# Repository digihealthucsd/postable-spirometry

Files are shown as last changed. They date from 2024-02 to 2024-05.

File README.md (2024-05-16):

# postable-spirometry: User-Assembled Vortex Whistle Spirometer

## About Project:
3D printed vortex whistles have been shown to be an accessible alternative to clinical spirometers, the most common pulmonary function test to assess lung health. While more accessible than the current standard, the question remains of how to get the whistles to users for their own personal use. The novelty of this project is the proposal and demonstration of our idea of making the vortex whistle out of a postcard so it can be simply mailed to users. This work demonstrates the potential for a spirometer system to be mass-deployed in the form of a postcard. The results demonstrate that the use of oilboard does not compromise the performance of the device, and can thus serve as a mass-screening tool. As such, Postable Spirometry can serve as a truly ubiquitous pulmonary function testing solution. This work inspires the larger vision that other smartphone accessories or attachments can also be constructed out of paper, creating a fleet of Postables. Postables will enable the wide scale deployment of ubiquitous smartphone accessories.

## About this repo:
In an effort to open source our work to share our progress with others, this repo contains software [coming soon!] used for analysis (frequency to flow velocity pipeline) as well as the hardware designs. The laser cut designs, and settings to print with, can be viewed and accessed by users. Feel free to print these designs on your own machines and try it out!

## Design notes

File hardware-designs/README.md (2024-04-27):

# FILES

The "hardware-designs" folder contains the following folders and contents:

* .../3d-print: Solidworks and STL files for 3D printed version of the vortex whistle
* .../dxf: Drawing files which can be used for laser cutting of the Oilboard and Sticker Paper parts
* .../postcard: Single SVG file with the main oilboard components and QR code for the postcard
* .../solidworks: Solidworks part and drawing files of the whistle components
* .../assembly-guide: Example assembly guide for the postcard design

# DESIGN

## Main Design

The Oilboard Core and Sticker Paper Outlet Skin files comprise the drawings needed for the laser cut components of the low cost vortex whistle. All dimensions were initially based upon the spirocall paper (https://dl.acm.org/doi/10.1145/2858036.2858401), but has been slightly modified through iterations of the project. They generally remain similar to their original dimensions in the Spirocall paper. Additionally, a funnel component exists to adapt the whistle inlet to a conventional spirometer inlet/ mouthpiece size.
\
\
In order to created a more streamlined process for users, the postcard design contains all needed pieces in a single image file. An example can be found [here](postcard) (at ".../postcard/postableSpirometry.svg"). Additionally, this postcard design could include a QR code which links to an assembly guide to aid users in assembly of the whistle.
\
\
The process of assembly consists of taking the oilboard core pieces and putting them together in the same shape as a 3D printed vortex whistle model. To tape pieces together and seal connections to be airtight, use waterproof medical adhesive tape (very thin, flexible, amazon link below for reference). The sticker paper is used to seal the outlet of the whistle and join it to the top face of the whistle (labeled base 3). An example assembly guide can be found [here](assembly-guide) (at ".../assembly-guide")

## Components

The oilboard core is the primary structure for the whistle. It consists of the following parts:

* Base 1: Main section/body of the whistle which is folded into a cylidrical shape, joining the 35mm sides.
* Base 2: Lower face of the whistle which joins to base 1. No internal circle.
* Base 3: Upper face of the whistle which join to base 1 and the outlet. Has internal circle for outlet.
* Outlet: Outlet nozzle which sits on top of base 3. Fold to join the 27mm sides
* Inlet: Inlet nozzle with tabs to fold outward to seat better in the main whistle body, and also create the needed angle for the entering air. The two thinner tabs are to be joined together when folding the inlet and face the top of the whistle when the inlet is seated in base 1 (through the small hole cutout).
* Funnel: Funnel component to slot over the whistle inlet and adapt it to a larger spirometer mouthpiece size

The sticker paper skin for the outlet replaces a thin tape seal on the outlet, and also has tabs which are folded back during construction. When joining base 3 and the outlet, these sticker paper tabs hold both pieces together, before the thin tape is added on top for a better air seal. 

## Materials

The following information is additional information in regards to the material and laser cut settings used in the project:

* Oilboard: N/A
* Sticker paper: PPD-36
* Laser Cutter: Epilog Laser Cutter

### Epilog Laser Cutter Software Material Configurations:

Oilboard Settings: Oilboard vector preset: 
* Power: 50
* Speed: 45  
* Frequency: 5

Sticker Paper Settings: 
* -Power: 100
* -Speed: 65  
* -Frequency: 5

### Other Materials Notes

Ensure that the glossy side is facing down on the laser cutter (the paper side should face the laser beam). This helps to ensure the cut goes through properly.

Amazon Link to waterproof medical adhesive tape: https://www.amazon.com/Transparent-Adhesive-Waterproof-Bandages-Dressing/dp/B08CXMCPG7/ref=sr_1_15?keywords=medical+tape+waterproof&qid=1692652463&sr=8-15

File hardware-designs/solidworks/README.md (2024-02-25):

The "Solidworks" folder contains the following types of files:

* .SLDDRW: Main drawing files which can be used to create the laser cutter drawings of the whistle components
* .SLDPRT: Dependency files referenced in the .SLDDRW files for the drawings of Oilboard core components

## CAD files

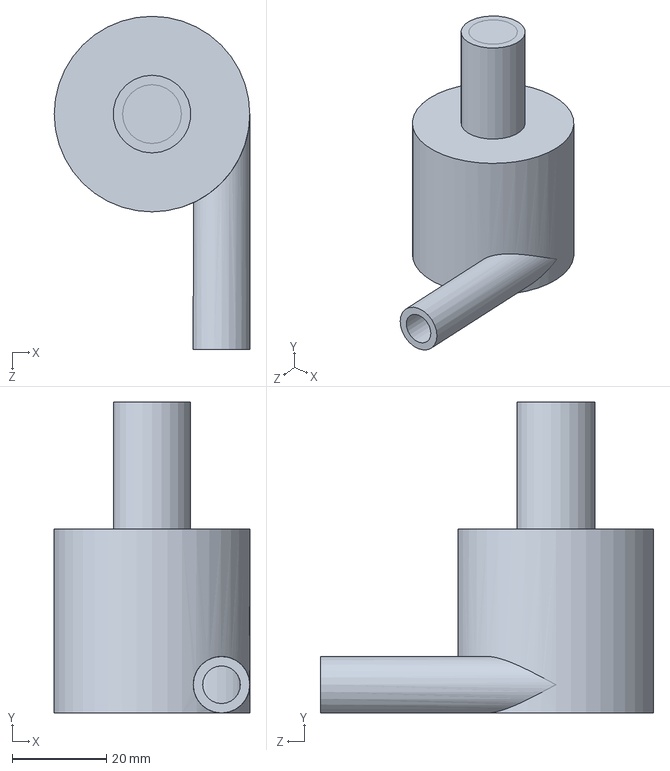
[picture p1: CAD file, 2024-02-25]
hardware-designs/3d-print/3D Print Vortex Whistle.SLDPRT
41.5 x 66.0 x 70.8 mm

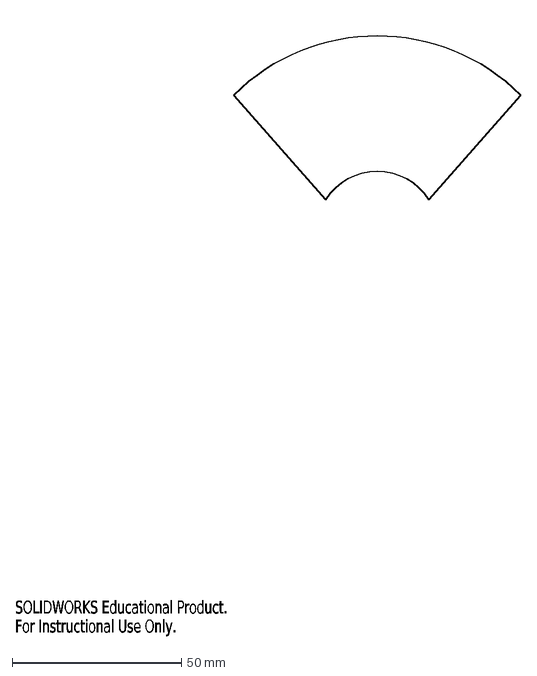
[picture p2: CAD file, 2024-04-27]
hardware-designs/dxf/Funnel.DXF
SOLIDWORKS Educational Product.
For Instructional Use Only.

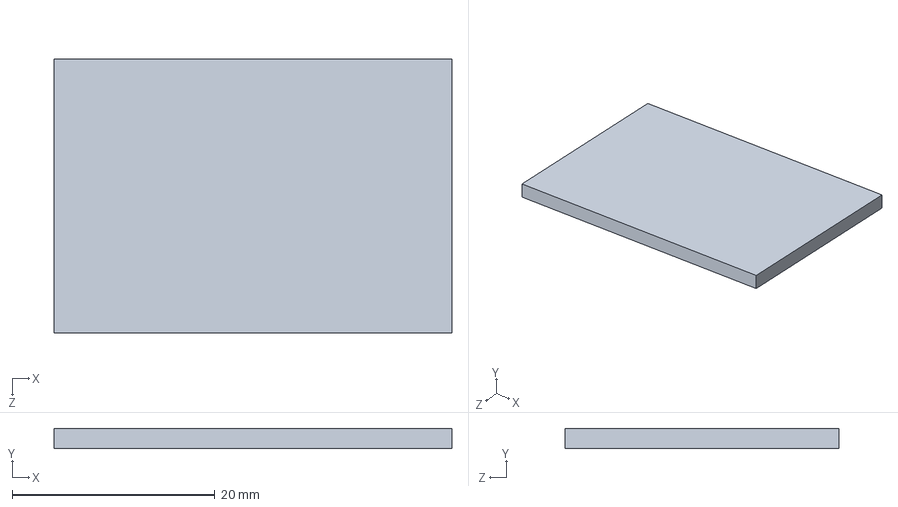
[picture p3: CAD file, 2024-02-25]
hardware-designs/solidworks/Core Outlet.SLDPRT
39.3 x 2.00 x 27.0 mm

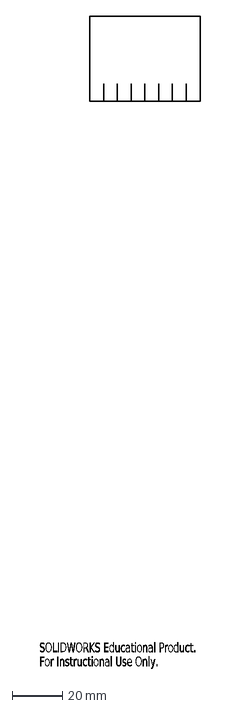
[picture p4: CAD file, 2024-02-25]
hardware-designs/dxf/Sticker Paper Outlet Skin Laser Cut Template.DXF
SOLIDWORKS Educational Product.
For Instructional Use Only.

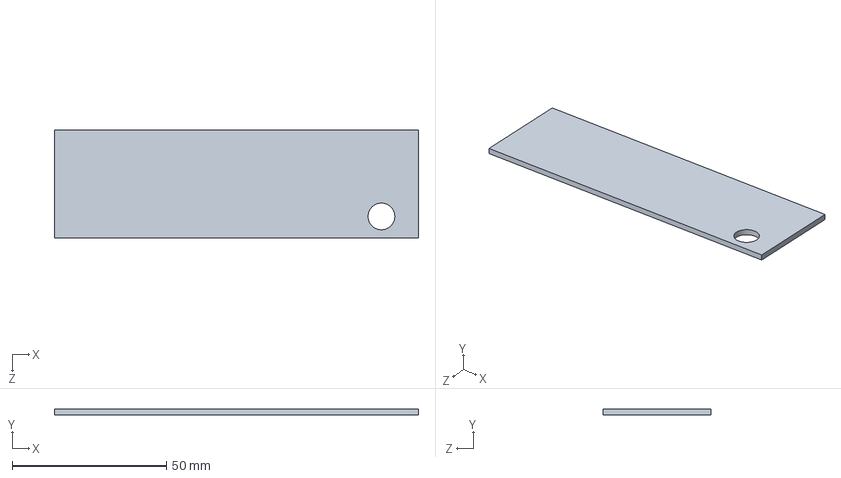
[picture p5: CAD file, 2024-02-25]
hardware-designs/solidworks/Core Base 1.SLDPRT
117.8 x 2.00 x 35.0 mm

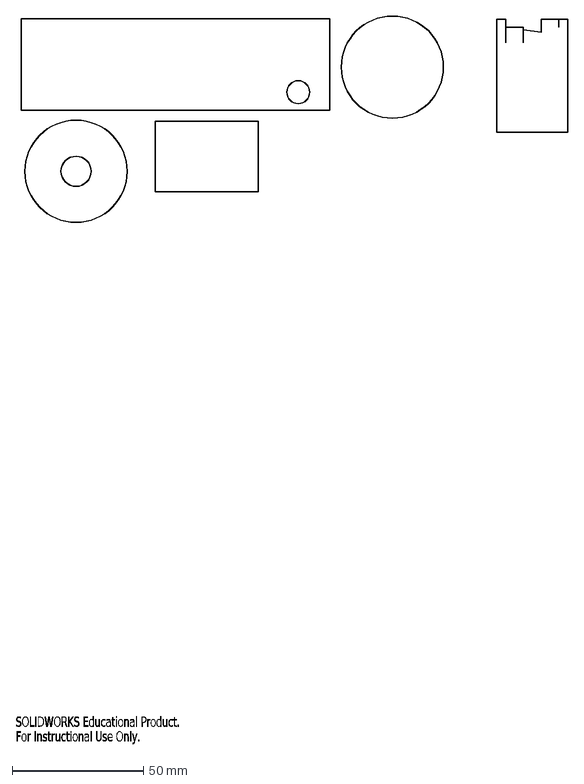
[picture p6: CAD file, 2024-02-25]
hardware-designs/dxf/Oilboard Core Laser Cut Template .DXF
SOLIDWORKS Educational Product.
For Instructional Use Only.

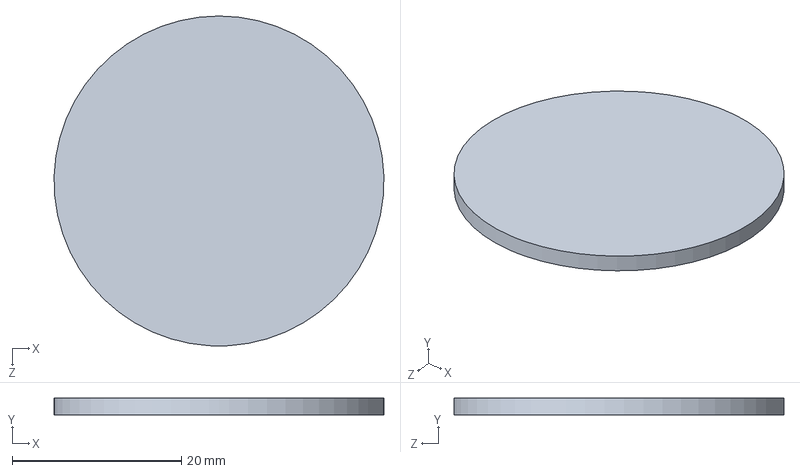
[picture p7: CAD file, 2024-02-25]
hardware-designs/solidworks/Core Base 2.SLDPRT
39.0 x 2.00 x 39.0 mm

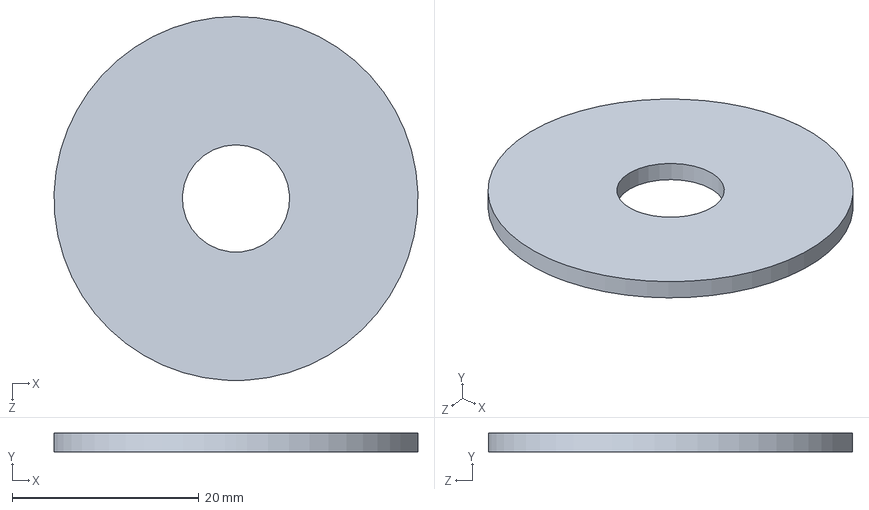
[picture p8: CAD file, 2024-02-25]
hardware-designs/solidworks/Core Base 3.SLDPRT
39.0 x 2.00 x 39.0 mm

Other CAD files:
hardware-designs/3d-print/3D Print Vortex Whistle.STL
hardware-designs/solidworks/Funnel.SLDDRW
hardware-designs/solidworks/Oilboard Core Laser Cut Template .SLDDRW
hardware-designs/solidworks/Sticker Paper Outlet Skin Laser Cut Template.SLDDRW

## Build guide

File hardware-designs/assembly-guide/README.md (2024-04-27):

# Introduction

This assembly guide contains a potential assembly process for creating a postable vortex whistle. This guide contains the steps needed to create a model using only waterproof tape, and an alternative step if the sticker paper cover for the outlet is instead used.

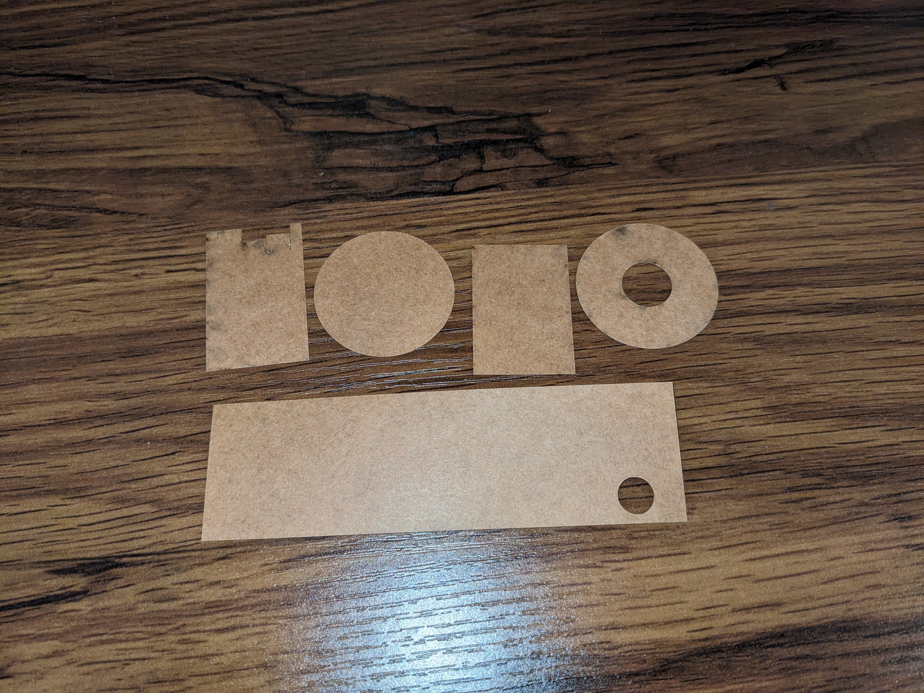
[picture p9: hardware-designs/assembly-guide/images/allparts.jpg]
all_parts


* Starting layout of all oilboard core components

# Assembly Guide

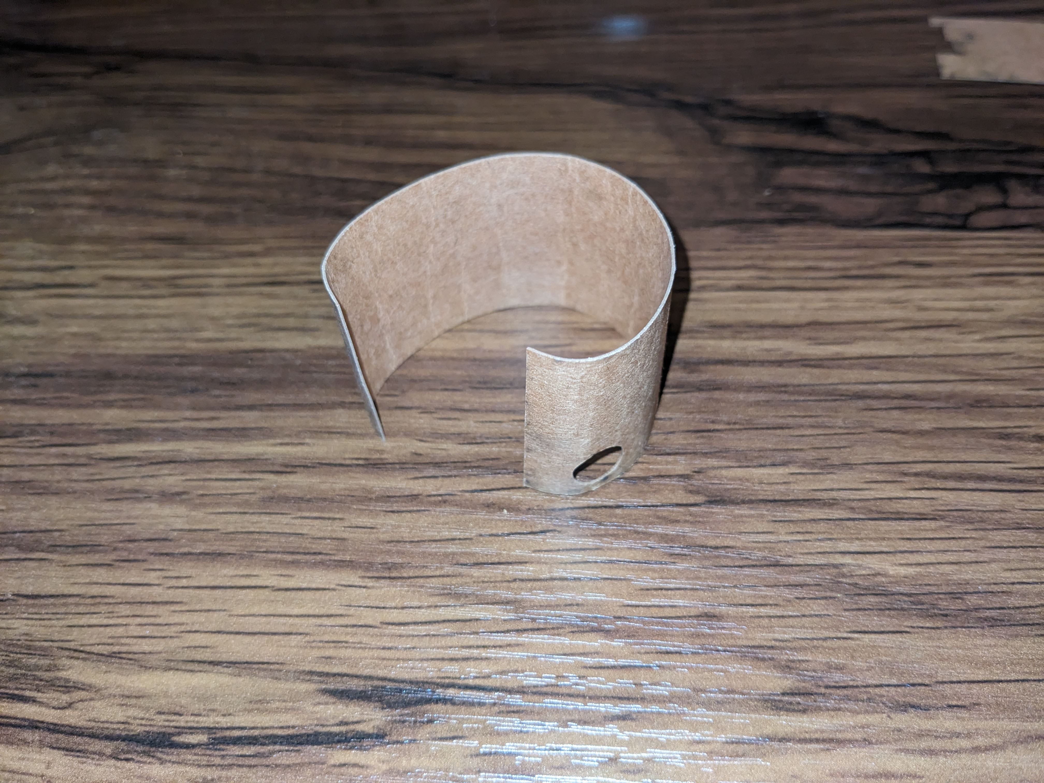
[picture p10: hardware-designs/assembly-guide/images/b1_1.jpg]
fold_body_1

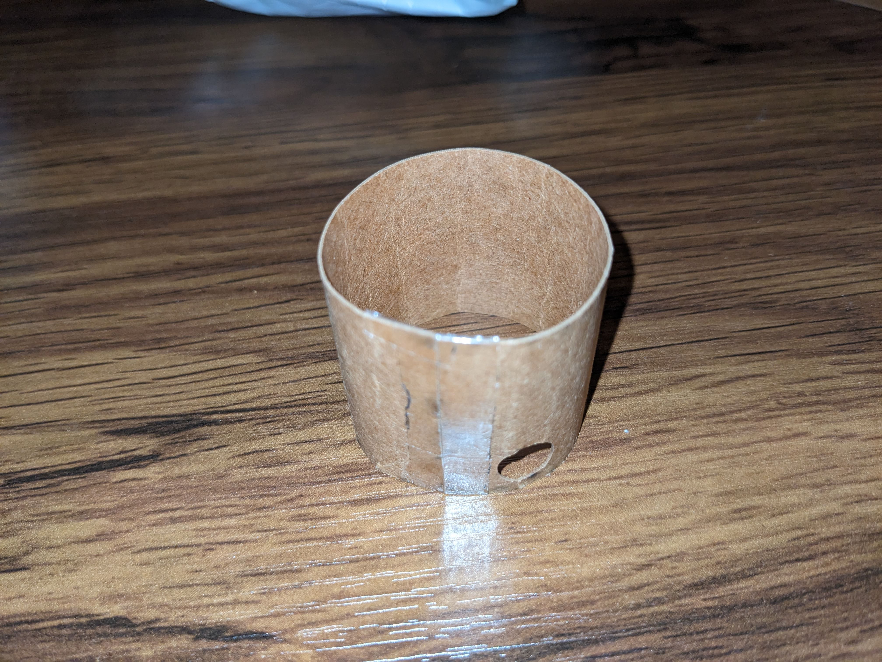
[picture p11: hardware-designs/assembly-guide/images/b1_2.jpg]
tape_body_1


1. Start by folding the main whistle body (body-1 component) piece, then tape the gap to form a cylinder

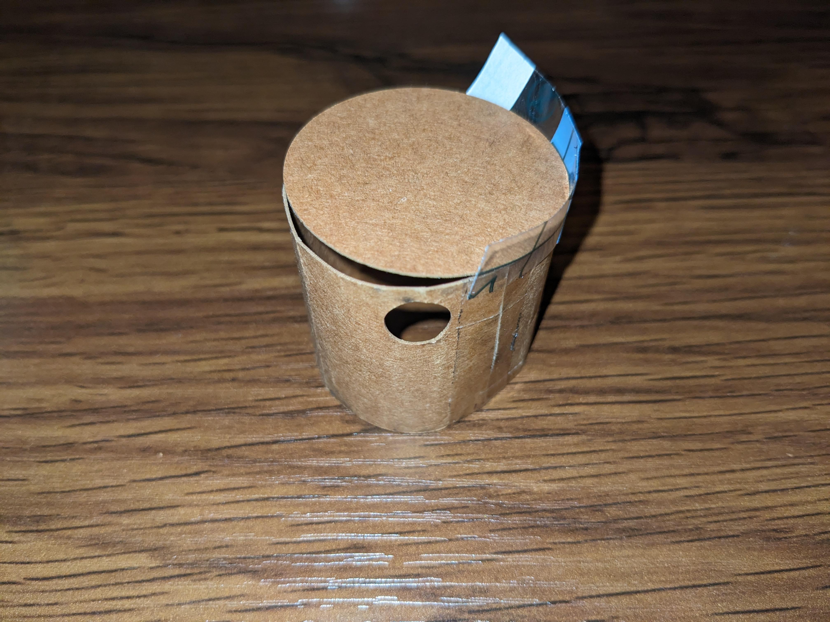
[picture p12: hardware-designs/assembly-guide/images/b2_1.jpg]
tape_body_2

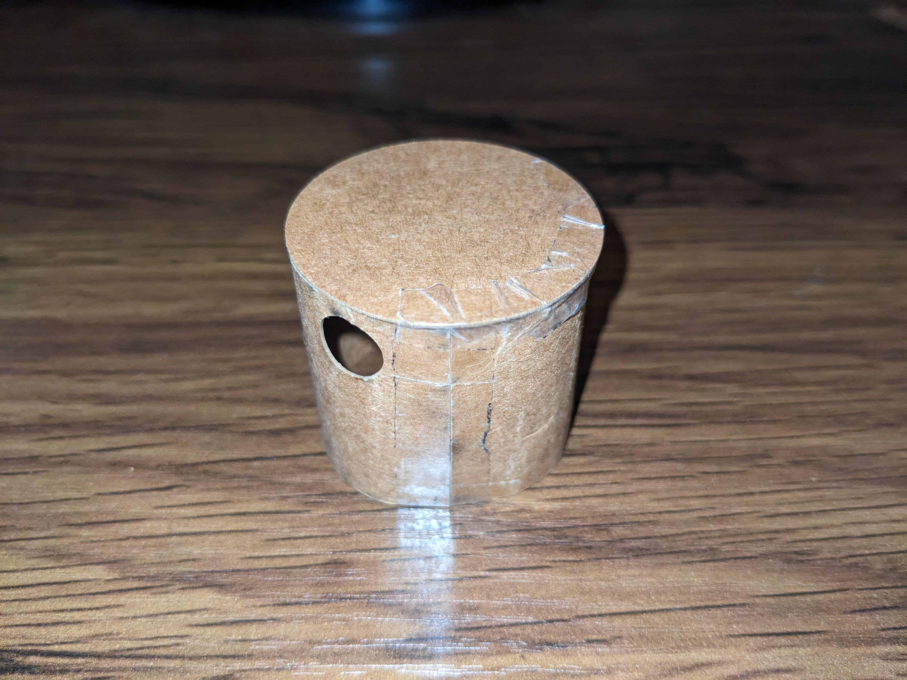
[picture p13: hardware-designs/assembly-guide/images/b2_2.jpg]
seal_body_2


2. Place the lower base (body-2 component) piece on the whistle main body and add tape. Fully seal the seam/gap between the pieces

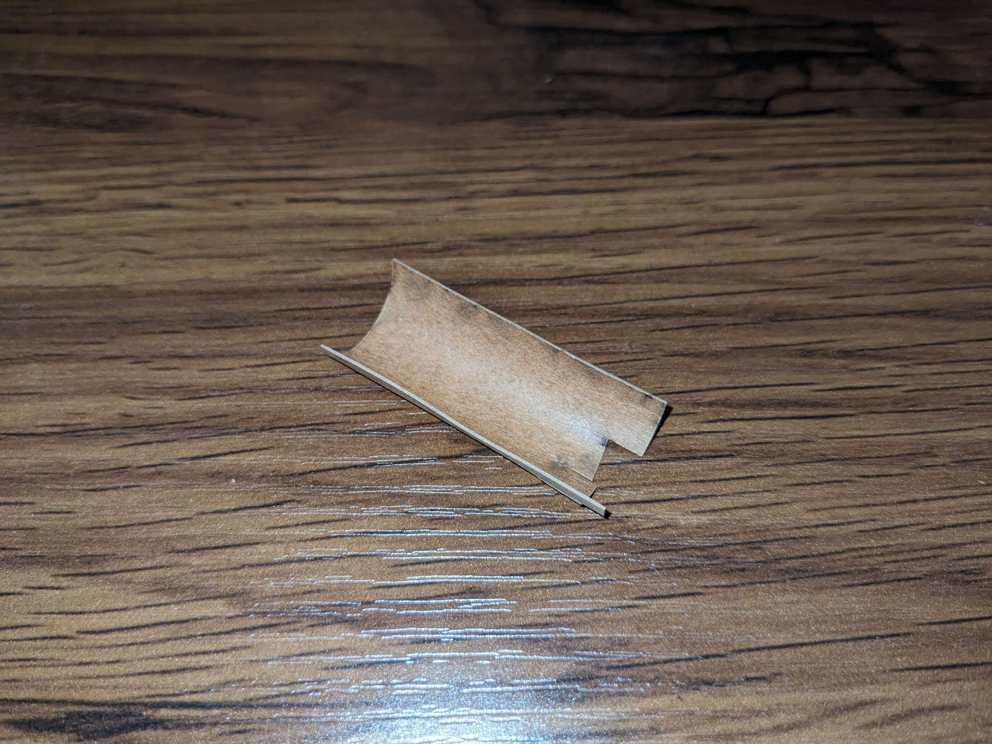
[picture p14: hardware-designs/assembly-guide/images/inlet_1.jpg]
fold_inlet

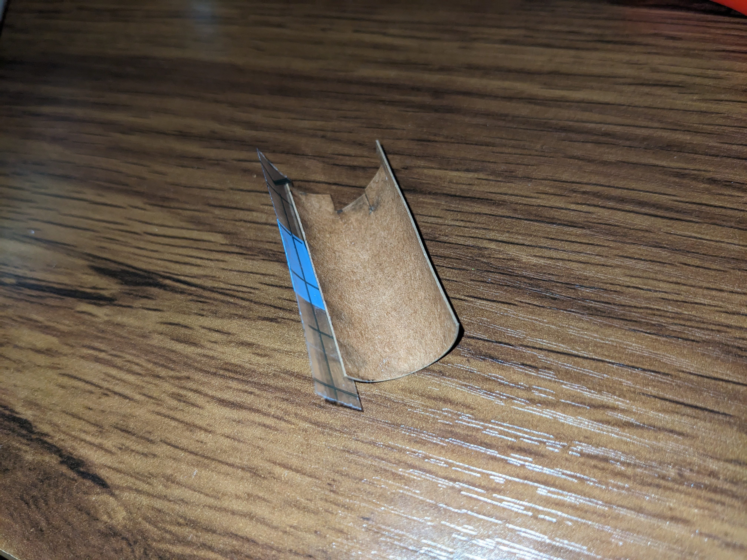
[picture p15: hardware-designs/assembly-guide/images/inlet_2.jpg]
seal_inlet

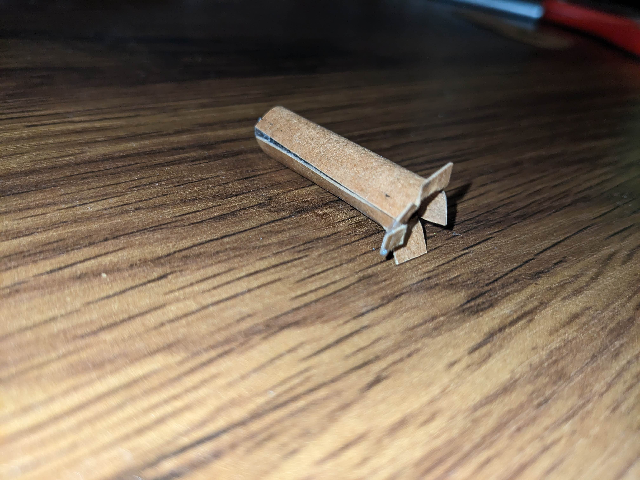
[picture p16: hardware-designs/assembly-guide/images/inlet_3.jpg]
bend_inlet_tabs


3. Fold the inlet piece, seal the main seam to form the cylinder shape of the inlet and then bend the tabs back slightly (this will help with seating the inlet later on).

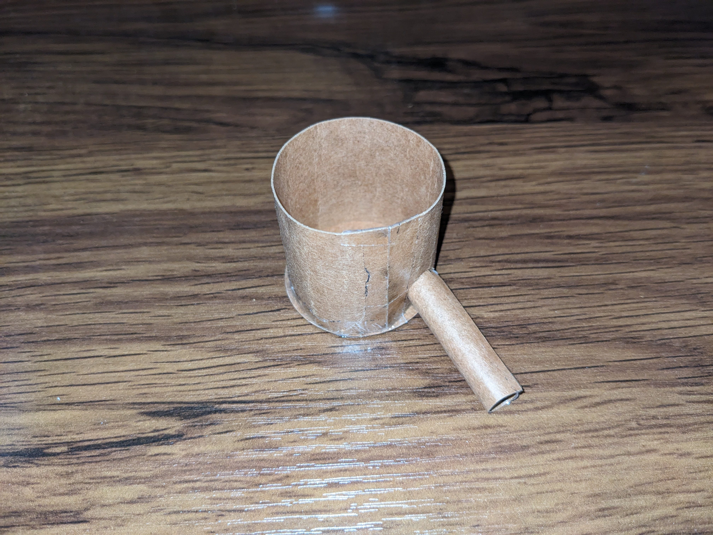
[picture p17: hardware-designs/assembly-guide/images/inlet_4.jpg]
insert_inlet


4. Insert the inlet into the main body piece through the small hold in the main body, being careful not to damage the seal between the main body and lower base. This may require bending the tabs of the inlet slightly to have the inlet fit through the hole.

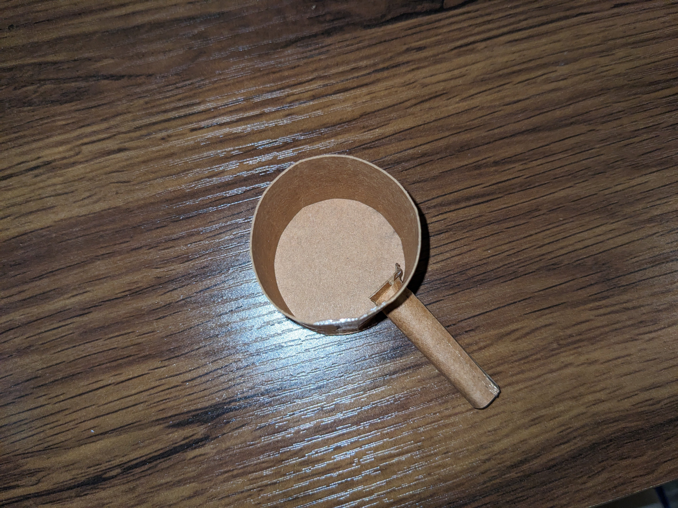
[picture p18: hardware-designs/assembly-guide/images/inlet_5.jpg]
bend_inlet_tabs_back


5. Once the inlet is passed through the hold in the body, press the tabs back outward, and make them flush with the inner wall of the main body.

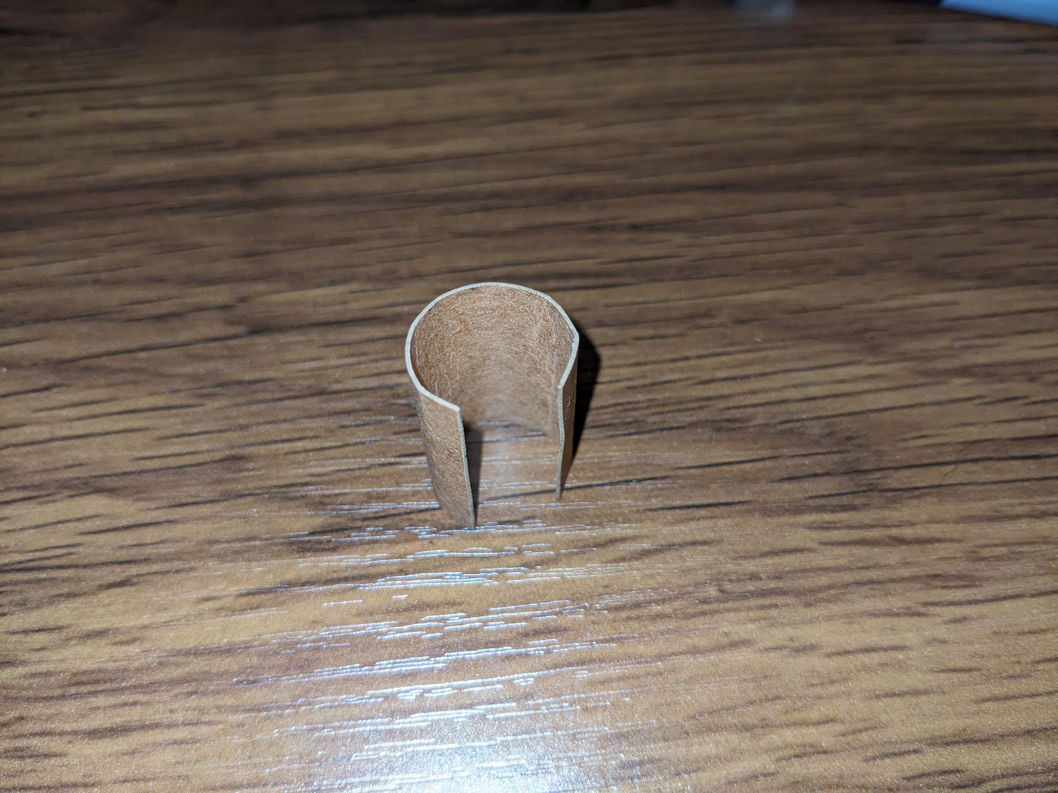
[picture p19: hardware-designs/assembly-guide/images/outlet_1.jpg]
fold_outlet

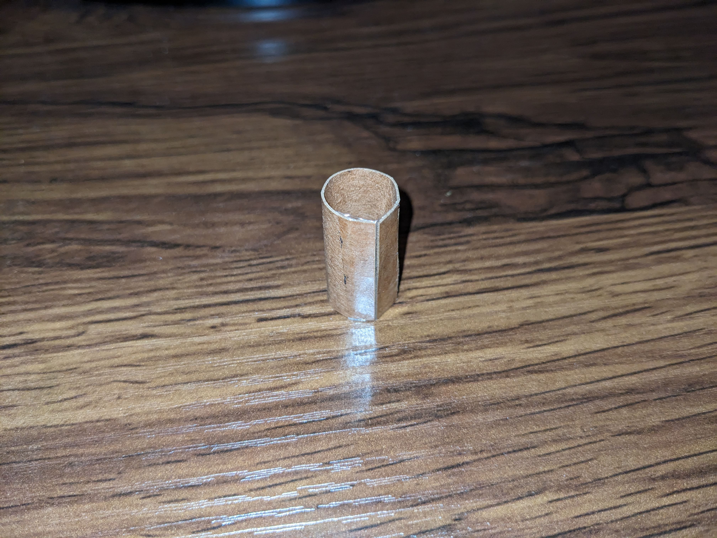
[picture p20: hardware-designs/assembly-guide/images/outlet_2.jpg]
seal_outlet


6. Fold the outlet and seal the seam to form a cylinder.

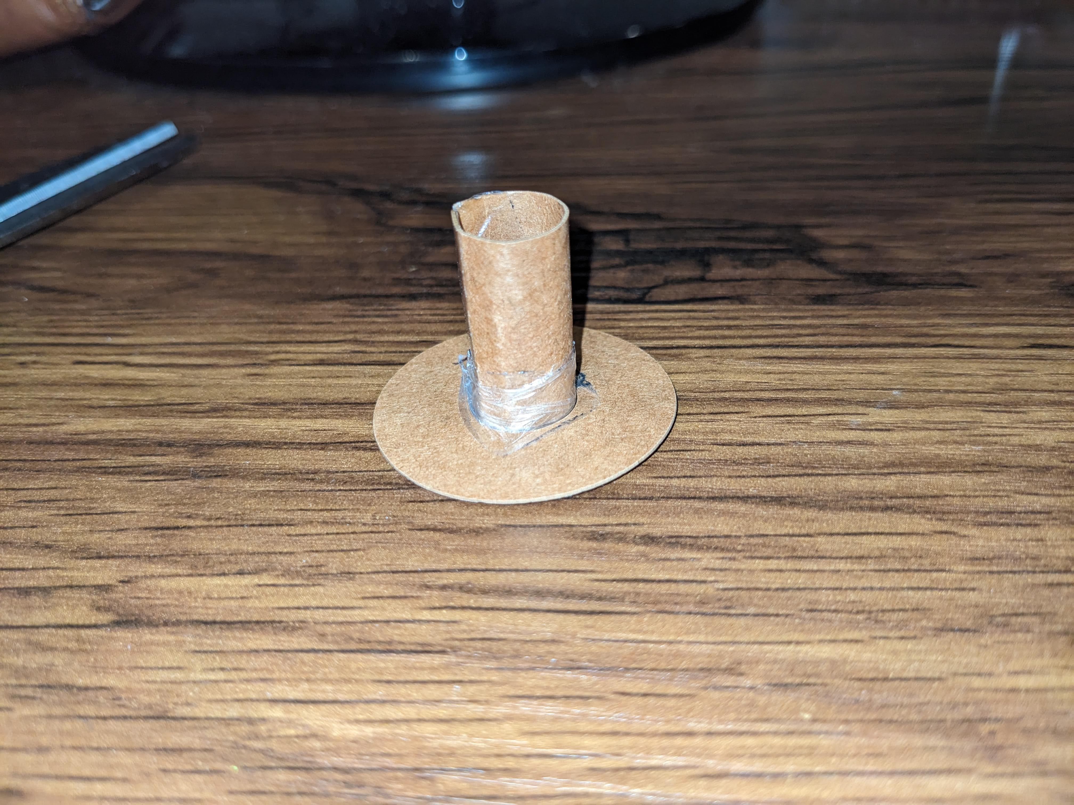
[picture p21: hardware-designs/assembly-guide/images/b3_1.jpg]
join_outlet_body3


7. Tape the outlet to fit over the inner hole of the upper base (body-3 component) of the whistle.
   * (Optional) If desired for use, the sticker paper skin can be instead applied around the outlet, with the tabbed pieces folded back. When joining these pieces, the tabs will be flush with and stick to the surface of the upper base. Tape can then be applied over the same seam of the components to ensure a proper seal between the upper base and outlet.

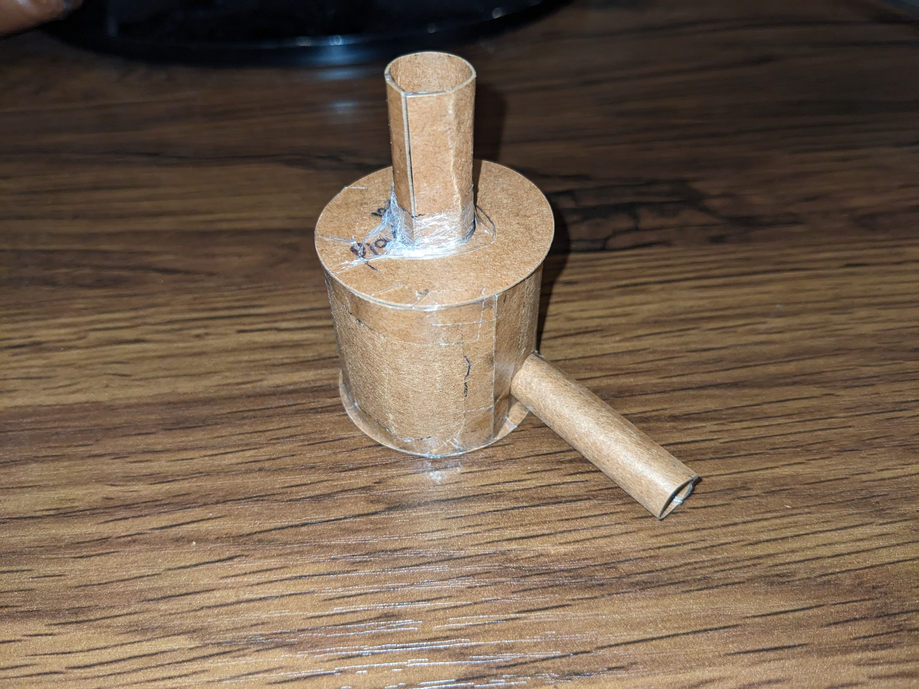
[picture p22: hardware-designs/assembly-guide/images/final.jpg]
finish_whistle
  

8.  In a similar process to the lower base (body-2) component, tape the upper base piece to the top of the main body, ensuring no gaps.
   * To increase air tightness of the device, tape can be added around the gap between the inlet and the main body if desired.

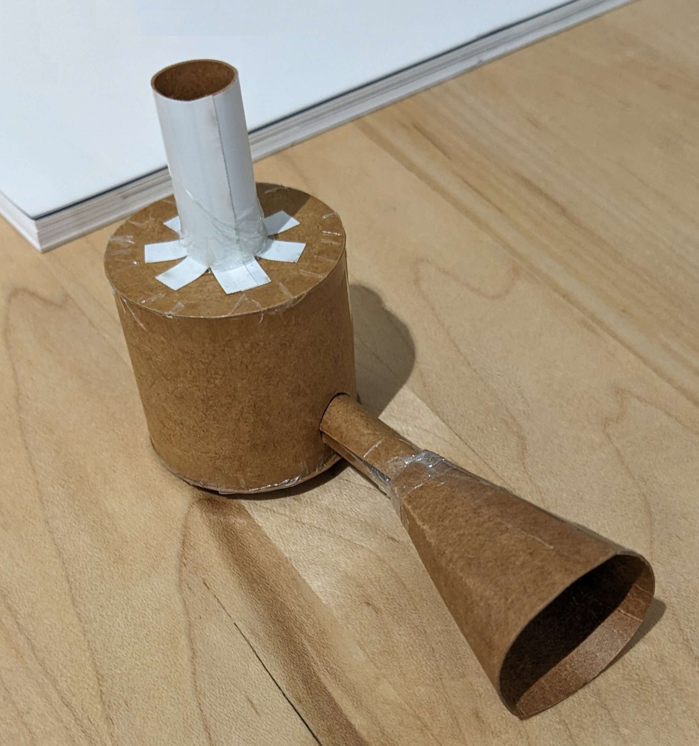
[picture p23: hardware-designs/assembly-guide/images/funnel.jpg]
funnel


9. (Optional) If desired, the funnel component can be used by folding and sealing the edges of the laser-cut piece, then by sliding the narrow end over the inlet of the whistle and sealing the connection with tape.

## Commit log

2024-02-25 Added hardware files and READMEs
    [3D Print Vortex Whistle.SLDPRT, 3D Print Vortex Whistle.STL, Core Base 1.SLDPRT, Core Base 2.SLDPRT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]
2024-04-02 Folder renaming, begin assemby guide
    [3D Print Vortex Whistle.SLDPRT, 3D Print Vortex Whistle.STL, Core Base 1.SLDPRT, Core Base 2.SLDPRT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]
2024-04-02 Preliminary assembly guide readme
2024-04-02 Updated hardware readme, draft assembly readme
2024-04-03 Updated assembly-guide README
2024-04-27 Added funnel files and update READMEs
    [Funnel.DXF, Funnel.SLDDRW]
2024-04-27 Added tags to assembly guide optional steps
